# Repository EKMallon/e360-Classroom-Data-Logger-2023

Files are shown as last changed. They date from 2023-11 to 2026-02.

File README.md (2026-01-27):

banner image
This program supports an ongoing series of DIY 'Classroom Logger' tutorials from Edward Mallon & Dr. Patricia Beddows at the Cave Pearl Project. The idea is to provide a starting point for student projects in environmental monitoring courses and/or thesis level research.</br>
The tutorial for this logger: [The e360: A Classroom Data Logger for Science](https://thecavepearlproject.org/2023/12/01/the-e360-a-10-classroom-data-logger-for-science/)</br>
has a companion video [2-Module Data Logger Build Video (90min w Commentary)](https://youtu.be/_LEFM4l9m5c)

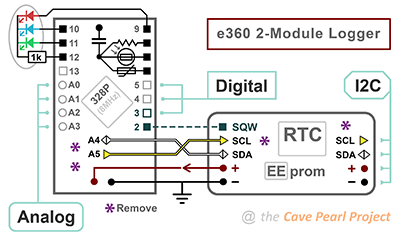
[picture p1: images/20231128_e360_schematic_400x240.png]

The code has support for a built-in NTC / LDR combination, Bmp280, BH1750, and PIR sensors. These are enabled / disabled by uncommenting define statements at the beginning of the code. Each sensor enabled after the single-byte LowBat & RTCtemp defaults contributes two additional bytes per sampling event because every sensor reading gets stored in a 16-bit integer. The total bytes per saved per record must total 1, 2, 4, 8 or 16 only. Modifying the logger base code for a new type of sensor requires edits only at the areas indicated by call out numbers on the following flow charts. These are labeled with comments: STEP1, STEP2, STEP3, etc. so you can locate those sections with the Find function in the IDE.  They are surrounded by rows of ++PLUS++ symbols:</br>
>//++++++++++++++++++++++++++++++++++++++++++++++++++++</br>
>// STEP1 : #include libraries & Declare Variables HERE</br>
>//++++++++++++++++++++++++++++++++++++++++++++++++++++</br>
</br>


If all you do is enable the supported sensors via defines at the start of the program you won't have to deal with the low-level storage details.


 However to add new sensors you'll need to understand the I2C transaction that transfers those sensor readings into the EEprom at the end of the main loop. This involves dividing your sensor variables into 8-bit pieces and adding those bytes to the wire transfer buffer. This is accomplished with bit-math operations or via the lowByte & highByte macros.  The general pattern when sending bytes to an I2C EEprom is:</br>

```
Wire.beginTransmission(EEpromAddressonI2Cbus);
Wire.write(highByte(memoryAddress));
Wire.write(lowByte(memoryAddress));
loByte = lowByte(SensorReadingVariable); Wire.write(loByte);
hiByte = highByte(SensorReadingVariable); Wire.write(hiByte);
```

**add more Wire.write statements here as needed**  
You can ONLY add a total of 1, 2, 4, 8 or 16 DATA bytes to the I2C transaction. Powers of two increments are required because the recorded data must align with page boundaries inside the EEprom.

```
Wire.endTransmission();
```

The key insight here is that the wire library is only loading a memory buffer until Wire.endTransmission() is called. So it does not matter how much time you spend doing calculations, or slicing the variables, so long as you don't try and start another I2C transaction while you are still in the middle of this one. Once that buffer is physically sent over the wires, the EEprom enters a self-timed writing sequence and the logger reads the rail voltage while the CR2032 is under load. </br>

The data download function in setup retrieves those separate bytes and concatenates them back into the original integers - so the sequence of operations in the sendData2Serial function -STEP6- must exactly mirror the byte-order used to load the EEprom in the main loop.

---

In 2026: New configuration options were added to the start-up menu [ accessed via the IDEs Serial Monitor window ] 
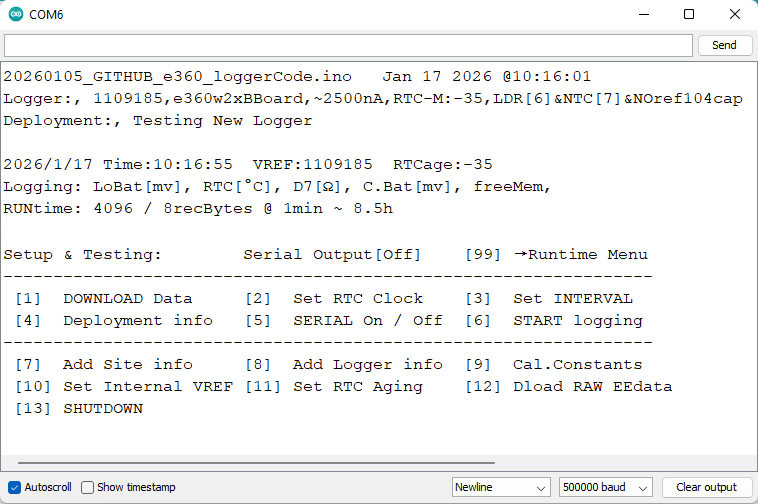
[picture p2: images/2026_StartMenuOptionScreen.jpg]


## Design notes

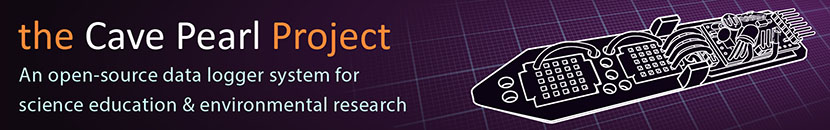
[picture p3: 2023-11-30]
images/GitHubHeader_830x130_20231128.jpg

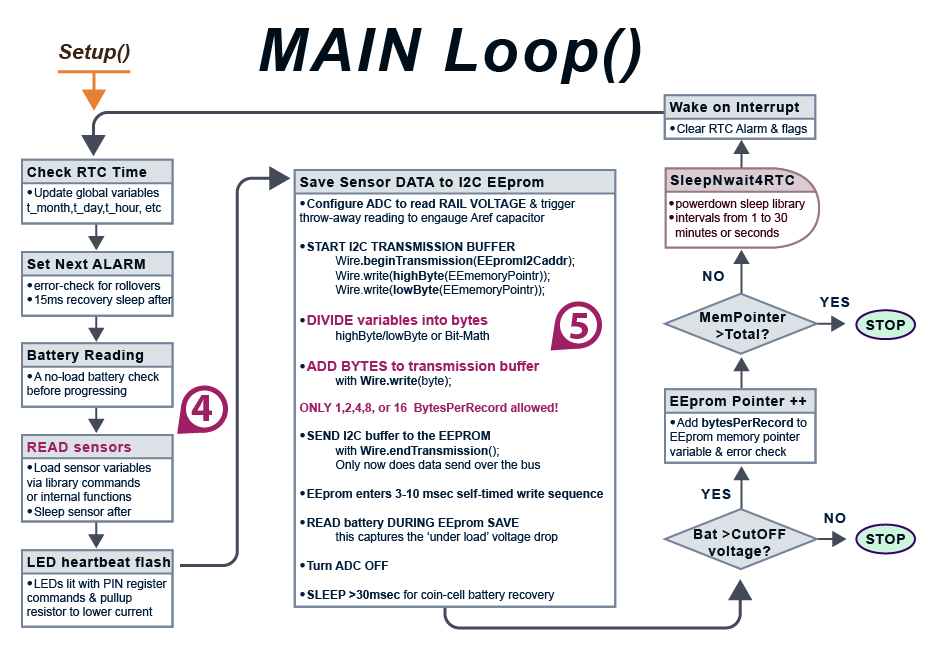
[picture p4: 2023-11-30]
images/2023_e360_LOOP_flowChart.png

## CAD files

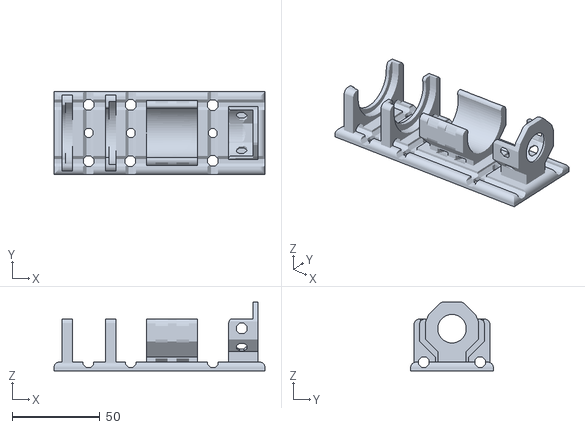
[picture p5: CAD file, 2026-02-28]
UniMountV6_30&50ml_byEKM_2025.stl
120.0 x 47.0 x 39.2

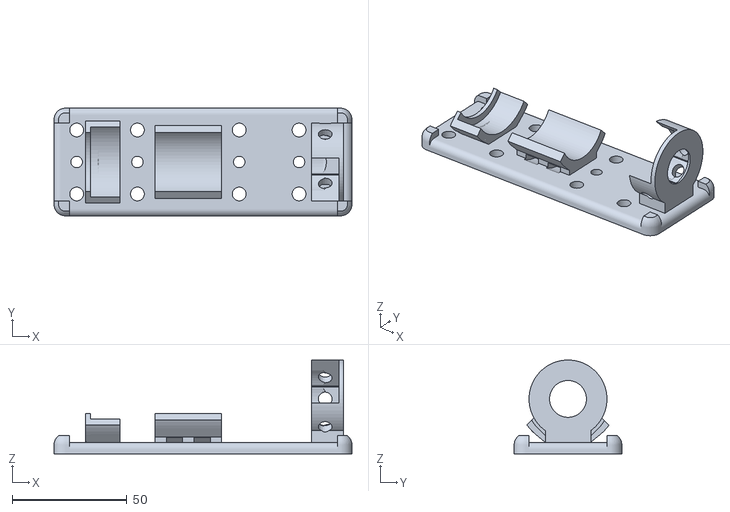
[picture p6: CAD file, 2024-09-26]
e360_MountingBracket_V10_byEM_240925.stl
130.0 x 47.0 x 41.0

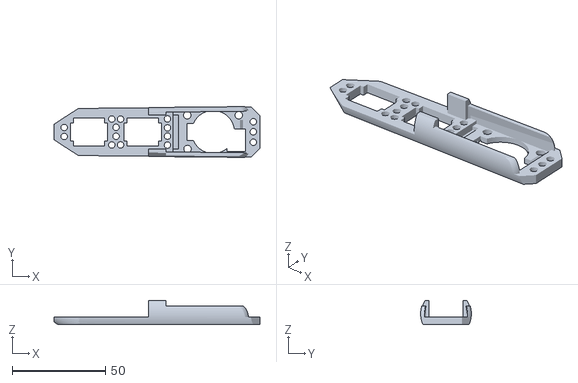
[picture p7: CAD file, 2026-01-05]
20260101_e360_2xBBoardRailwSides.stl
110.6 x 27.3 x 13.0

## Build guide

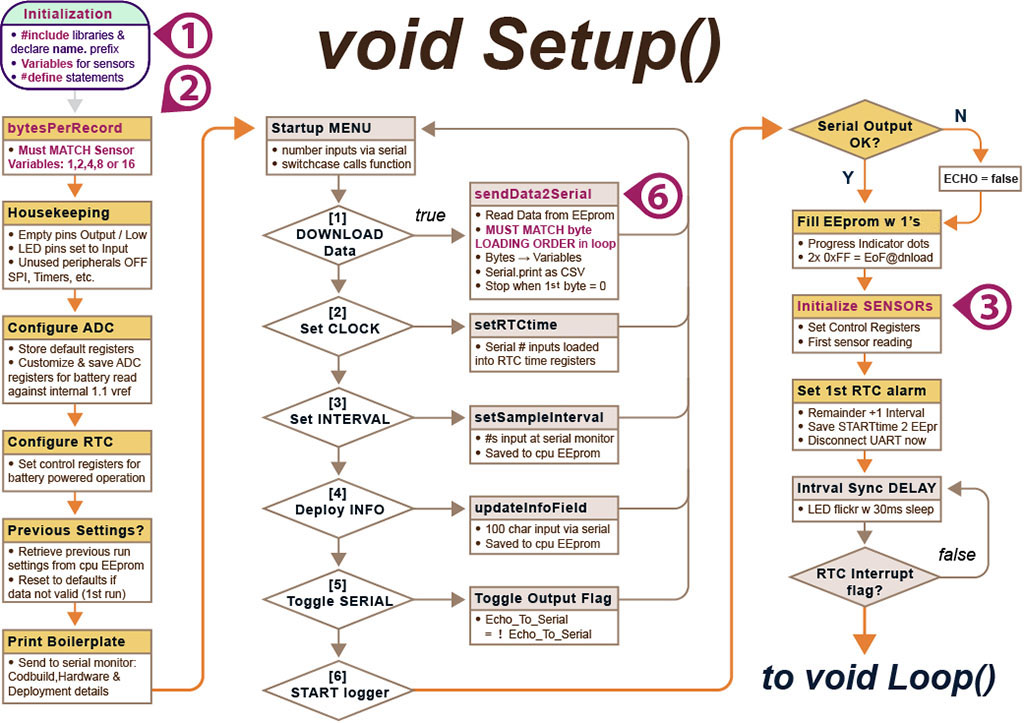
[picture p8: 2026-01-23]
images/2026_SETUP_flowChart_JPEG.jpg

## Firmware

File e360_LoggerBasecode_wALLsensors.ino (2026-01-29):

// 2-module logger code by Edward Mallon - modified 2023 for the e360 course at Northwestern University
// https://thecavepearlproject.org/2023/12/01/the-e360-a-classroom-data-logger-for-science/
/*
This program supports an ongoing series of DIY 'Classroom Logger' tutorials from the Cave Pearl Project. 
The goal is to provide a starting point for self-built student projects in environmental monitoring.
This low power 2-module iteration runs from a CR2032 coin cell and uses EEprom memory to store sensor readings. 
Data download & logger control are managed through the IDE's serial monitor window at 500000 baud. 
The logger WILL NOT START until those serial handshakes are completed via a UART connection.
The most important rule to follow when adding new sensors is that this code can only accept 1, 2, 4, 8 or 16 sensorBytesPerRecord.
These 'powers of 2' fit in the I2C buffer AND divide evenly into the EEproms hardware page size to prevent wrap-around.

The only library you MUST INSTALL for the minimum configuration of Promini & RTC module is LowPower [by LowPowerLab]
--------------------------------------------------------------------------------------------------------------------
  This can be INSTALLED via the Library Manager or from https://github.com/LowPowerLab/LowPower

The following sensors require library installations before they can be used:
---------------------------------------------------------------------------
  BH1750 LUX senso uses hp_BH1750  [by Stefan Armborst] via Lib Manager OR from https://github.com/Starmbi/hp_BH1750

  Sht30 Humidity sensor uses SHT85  [by Rob Tillaart] via Lib Manager OR from https://github.com/RobTillaart/SHT85/tree/master

  BMP280 uses BMP280_DEV  [by Martin Lindupp] which is available through the Lib Manager although the repo seems to have disappeared from github(?)

  BME280 (includes RH%) uses forcedBMX280  [by soylentOrange] which is available through the Lib Manager
  OR from https://github.com/soylentOrange/Forced-BMX280/tree/master NOTE that this library also works with the BMP280
  if you enable only recordBMEtemp_2byteInt and/or recordBMEpressure_2byteInt

*/
//++++++++++++++++++++++++++++++++++++++++++++++++++++++++++++++++++++++++++++++++   
//++++++++++++++++++++++++++++++++++++++++++++++++++++++++++++++++++++++++++++++++
// CURRENT 328p internal eeprom memory locations in use for start-up information
//++++++++++++++++++++++++++++++++++++++++++++++++++++++++++++++++++++++++++++++++   
//++++++++++++++++++++++++++++++++++++++++++++++++++++++++++++++++++++++++++++++++
/*
(0-3)     logger START TIME in unixtime (for reconstructiong timestamps later in sendSerial)
(4)       SampleIntervalMinutes
(5)       SampleIntervalSeconds
(6-9)     InternalReferenceConstant for calc. rail voltage from ADC in readRailVoltage
(10)      RTCagingOffset [adjusting by 3 compensates for ~ 1second of drift per month]
(12-15)   4byte UNIXtime of last time RTC was set by startMenu_setRTCtime - for drift tracking
(20-23)   Sensor starting paramaters usually stored from (24) onwards

FOUR 100-CHARACTER text info FIELDS also get stored in 328p internal eeprom:
Logger info:            64 to 164
Deployment info:        165 to 265
Calibration constants:  266 to 366
Site info:              367 to 467

These are output to screen by void setup_sendboilerplate2serialMonitor() when logger starts up
BUT you can store 'any' text in these fields, notes to self, normalization constants, etc
Note: we still have upper 512 bytes of 328p 1k eeprom availible for OLED screen fonts, etc.
// https://thecavepearlproject.org/2020/11/15/adding-two-oled-displays-to-your-arduino-logger-with-no-library/
*/

//++++++++++++++++++++++++++++++++++++++++++++++++++++++++++++++++++++++++++++++++   
//++++++++++++++++++++++++++++++++++++++++++++++++++++++++++++++++++++++++++++++++
// STEP0 :
// Create SENSOR definitions HERE to match the sensors you added to the logger
// Use these as global controls to enable/disable sensor code with #ifdef & #endif
// sensorBytesPerRecord for your sensor combination MUST TOTAL 1,2,4,8 or 16
//++++++++++++++++++++++++++++++++++++++++++++++++++++++++++++++++++++++++++++++++   
//++++++++++++++++++++++++++++++++++++++++++++++++++++++++++++++++++++++++++++++++

// LowestBattery & RTC_Temperature are the 2 byte 'base values' which are usually recorded with every sensor reading (as they require no extra sensor hardware beyond the logger itself)
#define logLowestBattery_1byte           // 1-byte (compressed): saves LowestBattery voltage recorded during EEprom saves
#define logRTC_Temperature_1byte         // 1-byte: the RTC's internal 0.25°C resolution temperature sensor

//Pressure sensor:
//#define readBMP280_Temp_2byte            // 2-bytes  // IF you enable all three BMP or BME outputs
//#define readBMP280_Pressure_2byte        // 2-bytes  // you will need two more bytes for an 8-byte record: try adding logLowestBattery_1byte & logRTC_Temperature_1byte 
//#define recordBMP280_Altitude_2byte      // 2-bytes: calculated by library

//Thermistor & Light Dependant Resistor
//#define readD7resistorwD8pullup_2byte    // NTC // 2-bytes:ohms // for explanation of the method for reading analog resistance with digital pins see
//#define readD6ResistorwD8pullup_2byte    // LDR // 2-bytes:ohms // https://thecavepearlproject.org/2019/03/25/using-arduinos-input-capture-unit-for-high-resolution-sensor-readings/
                                           // these have to match the connections shown in the build: https://thecavepearlproject.org/2023/12/01/the-e360-a-classroom-data-logger-for-science/
//Light/Lux sensor:
//#define readBh1750_LUX_2byte             // 2-bytes: NOTE: raw sensor output gets converted to Lux during download

//Infrared Motion sensor:                  // AM312 typically adds 10-15uA to sleep current
//#define PIRcountPerInterval_2byte  // 2-bytes:  PIR is just another interrupt generating sensor, saves # of PIR HIGH events in a specified sample interval. Do not enable this with PIRtriggersReadings_4byte - choose one or the other
//#define PIRtriggersReadings_4byte         // 4-bytes for full Unix Timestamp every pass: Do not enable this with PIRcountPerInterval_2byte - choose one or the other
// DOES NOT use the regular RTC-alarm based sampling interval but instead records the seconds elapsed between EVERY PIR trigger event in a uint32_t long variable [uint16_t would overflow at ~18 hours]
// PIRtriggersReadings_4byte usually enabled with four other bytes of sensor data [for a total of 8 bytes per record] OR with another 12 bytes of sensor data for a total of 16 bytes per record.
// WARNING this can use alot of memory very quickly if PIR is triggered frequently!  - recommend use with larger eeprom memory attached

//#define logCurrentBattery_2byte          // RARELY USED - not 1byte compressed like LowestBattery, primarily included as a powers-of-2 balancing option
//#define logFreeVariableMemory_2byte      // RARELY USED - primarily included as a powers-of-2 rule balancing option that does not rely on any external sensors

//#define readSi7051_Temp_2byte            // 2-bytes: used for NTC calibration - does not require a library, functions for si7051 at end of program

//#define readSht3x_Temp_2byte             // 2-bytes
//#define readSht3x_Humidity_2byte         // 2-bytes

//#define recordBMEtemp_2byteInt           // 2-byte NOTE: works with both BMP & BME
//#define recordBMEpressure_2byteInt       // 2-byte NOTE: works with both BMP & BME
//#define recordBMEhumidity_2byteInt       // 2-byte ONLY if BME 280 connected!

//#define OLED_64x32_SSD1306               // not a sensor, but enabled with define to include needed library - requires 1000uF rail cap to smooth noise from 1306 charge pump!

// Default EEprom: 0x57 & 4096 here saves data into the 4k eeprom on the RTC module:
#define EEpromI2Caddr 0x57                    // Run a bus scanner to check where your eeproms are https://github.com/RobTillaart/MultiSpeedI2CScanner
#define totalBytesOfStorage 4096              // Default: 0x57 / 4096bytes to use the 4k eeprom on the RTC module 

// If saving to an external 32k I2C EEprom module: 
//#define EEpromI2Caddr 0x50                  // Run a bus scanner to check where your eeproms are https://github.com/RobTillaart/MultiSpeedI2CScanner
//#define totalBytesOfStorage 32768           // Default: 0x57 / 4096bytes to use the 4k eeprom on the RTC module 

// NOTE: r9_b10_g11_gnd12 is the DEFAULT on the e360 logger for the Pulse Width Modulation lab
// the Red LED on D13 gets used if BOTH of the following LED #define statements are commented out
#define LED_r9_b10_g11_gnd12               // enables code for RGB indicator LED // expects a 1k limit resistor on shared GND!
//#define LED_GndGB_A0_A2                  // For 2022 2-module build with NO breadboards: red channel leg on led cut, A0gnd Green A1, blue A2, default Red on d13 left in place

#include <Wire.h>       // I2C bus coms library: RTC, EEprom & Sensors
#include <EEPROM.h>     // note: requires default promini bootloader (ie NOT optiboot)
#include <avr/power.h>  // library for shutting down 328p chip peripherals to lower runtime current
#include <avr/sleep.h>  // provides SLEEP_MODE_ADC to lower current during ADC readings in readRailVoltage() function
#include <LowPower.h>   // for interval & battery recovery sleeps
                        // from LowPowerLab (https://github.com/LowPowerLab/LowPower)

// Ref, Interval & Echo are reset via serial monitor input - so the values here don't matter
//-------------------------------------------------------------------------------------------------
int32_t InternalReferenceConstant = 1126400;  // default = 1126400L = 1100mV internal vref * 1024 // gets changed in setup via serial menu input option later
                                              // adding/subtracting 400 from the constant raises/lowers the 'calculated' result from readRailVoltage() by ~1 millivolt,
                                              // simply read the rail with a DVM while running on UART power and change the constant until the calculation is accurate
int8_t RTCagingOffset = 0;                    // stores -127 to +128 in the same two complement format that the register in the RTC uses
uint8_t SampleIntervalMinutes = 15;           // Allowed values: 1,2,3,5,10,15,20,30 for both - must divide equally into 60!
uint8_t SampleIntervalSeconds = 0;            // minutes must be zero for intervalseconds, seconds must be zero for intervalMinutes
                                              // NOTE: Make sure your sensor readings don't take longer than your sample interval!
                                              // If you over-run your alarm because the sensor took too long you will have to wait 24hours for next wakeup

bool ECHO_TO_SERIAL = false;                  // true enables multiple print statements throughout the code via if(ECHO_TO_SERIAL){} // also starts the run with no interval sync delay so timestamps are misaligned
bool displayMoreOptions = false;              // Flag toggle between Setup and Runtime Menus in void setup_displayStartMenu()

// most VARIABLES below this point stay the SAME on all machines:
//---------------------------------------------------------------------------
#define fileNAMEonly (strrchr(__FILE__, '/') ? strrchr(__FILE__, '/') + 1 : strrchr(__FILE__, '\\') ? strrchr(__FILE__, '\\') + 1 : __FILE__) //from: https://stackoverflow.com/questions/8487986/file-macro-shows-full-path
const char compileDate[] PROGMEM = __DATE__;  //  built-in function in C++ makes text string: Jun 29 2023
const char compileTime[] PROGMEM = __TIME__;  //  built-in function in C++ makes text string: 10:04:18
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

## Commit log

2023-12-02 Update e360_LoggerBasecode_wALLsensors.ino
    change sample interval variables to uint8_t
2023-12-18 sleepNwait4RTCalarm
    changed from
    LowPower.powerDown(SLEEP_15MS, ADC_ON, BOD_OFF);
    to
    LowPower.powerDown(SLEEP_FOREVER, ADC_OFF, BOD_OFF);
    If you see sleep currents in the 200uA range it's likely because the ADC was left on by accident
2024-01-09 void startMenu_setSampleInterval
    byteBuffer2 = SampleIntervalSeconds ? 60 % SampleIntervalSeconds : 0;
2024-02-29 ADC_OFF set to default during low power sleeps
    changed to
    LowPower.powerDown(SLEEP_15MS, ADC_OFF, BOD_OFF);
    in all areas except where ADC is being used
    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
2024-03-08 removed power_all_disable(); from void error_shutdown()
    as it was triggering high drain state on entering LowPower.powerDown(SLEEP_FOREVER
2024-04-09 Now with ADC looping during EEsave & changes to void error_shutdown()
    Looped ADC reads to catch lowest coincell voltage with larger eeproms.
2024-04-16 Removed ADC loops during EEsave
    Any rail voltage fluctuation during EEsave may cause chip to hang. This is very hard to debug. Now just two ADC readings and go to sleep during EEsave.
2024-04-18 Ignore first ADC reading after Wire.endTransmission();
    -occasionally throws a bad reading which can lead to logger shutdown
2024-06-05 Update e360_LoggerBasecode_wALLsensors.ino
    Added support for alternate LED connection.
    Added RTC stop flag warning & RTC oscillator shutdown in void error.
2024-06-28 Update e360_LoggerBasecode_wALLsensors.ino
    minor update conforming names in initial sensor defines
2024-07-16 Add files via upload
    50ml centrifuge tube rails for the e360 two module logger. With room for two mini breadboards.
    [20231201_e360_MiniBreadboardLoggerRails.stl]
2024-09-02 Add a Logger Mounting Bracket
    A Printable stl for a mounting bracket that allows the 50ml logger tube to be secured to a fence post; vertically or horizontally.
    [e360_MountingBracket_byEKM_240526.stl]
2024-09-15 Update e360_LoggerBasecode_wALLsensors.ino
    minor - change enabled sensors
2024-09-16 Update e360_LoggerBasecode_wALLsensors.ino
    Indicator LED control moved to separate functions (see end of code) Using port commands. Note LED channels lit with internal PULLUP resistors to limit current load on the coincell.
2024-09-18 Delete e360_MountingBracket_byEKM_240526.stl
    Delete old version, new version shortly.
    [e360_MountingBracket_byEKM_240526.stl]
2024-09-18 Add files via upload
    Mounting bracket tweaked for faster printing. Should print fine with no supports.
    [e360_MountingBracket_V3_byEM_240918.stl]
2024-09-26 Mounting Bracket
    Small updates to the spacing
    [e360_MountingBracket_V10_byEM_240925.stl]
2024-09-26 Delete e360_MountingBracket_V3_byEM_240918.stl
    Old design, new version uploaded.
    [e360_MountingBracket_V3_byEM_240918.stl]
2025-03-28 Update e360_LoggerBasecode_wALLsensors.ino
    ADDED Normalization Constants field and startMenu_updateLoggerInfoField is now unified function for all description info, ADDED support for sht3x sensors
2025-08-02 Update e360_LoggerBasecode_wALLsensors.ino
    Multiple small Updates: added logFreeVariableMemory_2byte for powers of two balancing option. ADDED void turnOnRedLED() which controls the D13 red on A2/3 LED configuration. readBattery() bugfix adde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
2026-01-05 Update e360_LoggerBasecode_wALLsensors.ino
    Removed parameter backup to simplify teaching codebuild. SERIAL On / Off moved to runtime options. Bugfix: LED routines for LED_r9_b10_g11_gnd12 failing to enable ground. Site info & Calibration info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
2026-01-05 Add files via upload
    Updated rails for more secure position holding inside the NUNC Thermo 50ml centrifuge tubes.
    Add conformal or nail polish to the sides before labeling so the marker doesn't bleed into the print layers.
    [20260101_e360_2xBBoardRailwSides.stl]
2026-01-05 Delete 20231201_e360_MiniBreadboardLoggerRails.stl
    New rail stl uploaded Jan 2026
    [20231201_e360_MiniBreadboardLoggerRails.stl]
2026-01-13 Update e360_LoggerBasecode_wALLsensors.ino
    changed pin states in initial Setup()
2026-01-23 Updated flow chart
    slightly different start menu in 2026
2026-01-23 Update README.md
    update flow chart
2026-01-25 Update e360_LoggerBasecode_wALLsensors.ino
    change default enabled sensors
2026-02-28 New logger mounting bracket for both e360 50ml centrifuge tubes
    This is universal mounting bracket that accommodates both 30ml (self standing Caplug) and 50ml (Thermo NUNC) centrifuge tubes. This gets used primarily for out-door sensor mounting and the NTC calibr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
    [UniMountV6_30&50ml_byEKM_2025.stl]

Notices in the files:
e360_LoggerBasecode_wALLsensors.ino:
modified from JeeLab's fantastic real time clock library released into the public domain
